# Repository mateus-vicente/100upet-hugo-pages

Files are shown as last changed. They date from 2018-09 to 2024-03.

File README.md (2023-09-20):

---
# 100µPET authors
---

# 100µPET Website

This repository contains the static website pages of the 100µPET project. The deployed website can be found
[here](https://100upet.web.cern.ch).

All commits to the master branch of this repository are automatically deployed to the EOS space of the project and thus
directly reflect on the published website.

## Dependencies

The website is generated from markdown files using the [hugo](https://gohugo.io/) compiler written in Go. In order to
install Hugo on your machine, pick the appropriate package or binary from
[the latest release](https://github.com/gohugoio/hugo/releases).

## Commands
The following commands might help adding content and testing the website locally before committing and deployment:

* __Start a local test server__
    ```sh
    hugo server -D
    ```
    The server will listen to [http://localhost:1313/](http://localhost:1313/).
    The additional command line argument `-D` also enables all documents currently in draft mode.

    Make sure to have the themes fetched as well (`git submodule init && git submodule update --recursive`).

    The repository has to be hosted on the CERN GitLab instance for the CI to work, and the pipeline on the ref has to be
    finished before the script can download the latest artifacts.

* __Add page to the main menu__

    See for example [content/docs/_index.md](./content/docs/_index.md) how to define a page to be in the main menu.

## Deploy Changes

Simply push to the `master` branch of this repository to get things published. It should be noted that only documents with
`draft = false` will be included in the published website.

## Updating Docsy & Prism

* __Docsy__
    To update Docsy (our hugo theme), run
    ```shell
    cd themes/docsy
    git fetch origin --prune
    git checkout origin/HEAD
    ```

* __Prism__
    To update Prism (our code highlighter), visit [this page][@prismdownload] and download `prism.js` and `prism.css` to the
    `static/js` and `static/css` folder respectively. Note that if you change any settings, make sure to update this README
    with the corresponding URL as well.

[@prismdownload]: https://prismjs.com/download.html#themes=prism-tomorrow&languages=clike+bash+c+cpp+cmake+ini+yaml&plugins=autolinker+show-language+toolbar+copy-to-clipboard

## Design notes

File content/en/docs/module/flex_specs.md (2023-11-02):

---
# SPDX-FileCopyrightText: 2022 100µPET
# SPDX-License-Identifier: CC-BY-4.0
title: "Flex Specifications"
weight: 2
---

Each "flex" (or Flexible Printer Circuit - FPC) will have 4 detection ASICs flip-chip bonded (in a 2x2 arrangement) with 300µm between each chip. Each FPC will host small 0201 SMD components in small regions close to the top and bottom peripheries of the 2x2 chip arrangement.

The width of the flex is 300 µm smaller than the width of the 2x2 chip arrangement (i.e. the ASIC hangs 150 µm beyond the flex on 2 edges), to allow an external cooling block to mechanicaly be in contact with the lateral edges of the chips for cooling optimization. 

The data lines and low-voltage power for the ASIC are routed via the a wide flex tail (to be connected to a ZIF connector (<a href="https://www.hirose.com/product/series/FH41">Hirose FH41 series</a>) on the TIM board), while the interface for the sensor biasing HV (200 V, <1 mA) is **yet to be decided**. 

| Main features                     |                                |
|:----------------------------------|:-------------------------------|
| Flex width                        | 60.6 [mm]                      |
| Width of flex's tail              | 20.5 [mm]\*                    |
| Length of flex's tail             | **TBC**                        |
| Number of layers                  | **TBC**                        |
| Number of layers on tail          | <4\*\*                          |
| Gap between ASICs                 | 300 [µm]                       |
| Bonding pads dimensions           | **TBC**\*\*\*                  |

\*See *Connector dimension table*, dimension *F* of connector with 40 pins, at <a href="https://www.hirose.com/en/product/document?clcode=&productname=&series=FH41&documenttype=Catalog&lang=en&documentid=D31607_en">this link</a> </br>
\*\*Single-chip test-flex is not flexible enought with 4 layers. Therefore, the flex's tail should have less. </br>
\*\*\*Pad can be round as the coined gold stud bumps with be smashed round and the diameter (160 microns) should match the uncertainty defined in the requirement for misalignment </br>

Below is the latest layout of the flex.
<object data="../100MuPET_FlexDim.pdf" type="application/pdf" width="100%" height="510px"><p>Here's a link to <a href="CleanCode.pdf">the PDF</a>instead.</p></object>

### Specs **TODO**:
- Shield plate at the back side of the flex with the footprint of the Bi-absorber layer: 
    - Should it be covered with Coverlay? 
        - If not should the Bismuth be glued with a thin adhesive conductive tape? In addition can we leave the Bismuth layer floating (given that the resistivity is 5 order of magnitude higher than copper)?
        - If yes likely to be glued/co-cured with a double-sided  conductive adhesive
    - Shield should be coupled to local ground of the module

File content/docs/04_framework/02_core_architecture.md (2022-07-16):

---
# SPDX-FileCopyrightText: 2022 CERN and the Allpix Squared authors
# SPDX-License-Identifier: CC-BY-4.0
title: "Architecture of the Core"
weight: 2
---

The core is constructed as a light-weight framework which provides various subsystems to the modules. It contains the part of
the software responsible for instantiating and running the modules from the supplied configuration file, and is structured
around five subsystems, of which four are centered around a manager and the fifth contains a set of general utilities. The
systems provided are:

1.  **Configuration**:
    The configuration subsystem provides a configuration object from which data can be retrieved or stored, together with a
    TOML-like \[[@tomlgit]\] parser to read configuration files. It also contains the Allpix Squared configuration manager
    which provides access to the main configuration file and its sections. It is used by the module manager system to find
    the required instantiations and access the global configuration. More information is given in
    [Section 4.3](.././03_configuration).

2.  **Module**:
    The module subsystem contains the base class of all Allpix Squared modules as well as the manager responsible for loading
    and executing the modules (using the configuration system). This component is discussed in more detail in
    [Section 4.4](.././04_modules).

3.  **Geometry**:
    The geometry subsystem supplies helpers for the simulation geometry. The manager instantiates all detectors from the
    detector configuration file. A detector object contains the position and orientation linked to an instantiation of a
    particular detector model, itself containing all parameters describing the geometry of the detector. More details about
    geometry and detector models is provided in [Section 4.5](.././05_geometry_detectors).

4.  **Messenger**:
    The messenger is responsible for sending objects from one module to another. The messenger object is passed to every
    module and can be used to bind to messages to listen for. Messages with objects are also dispatched through the messenger
    as described in [Section 4.6](.././06_messages).

5.  **Utilities**:
    The framework provides a set of utilities for logging, file and directory access, and unit conversion. An explanation on
    how to use of these utilities can be found in [Section 4.8](.././08_logging). A set of C++ exceptions is also provided
    in the utilities, which are inherited and extended by the other components. Proper use of exceptions, together with
    logging information and reporting errors, makes the framework easier to use and debug. A few notes about the use and
    structure of exceptions are provided in [Section 4.9](.././09_error_reporting).

[@tomlgit]: https://github.com/toml-lang/toml

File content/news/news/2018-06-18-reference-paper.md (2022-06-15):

---
# SPDX-FileCopyrightText: 2018 CERN and the Allpix Squared authors
# SPDX-License-Identifier: CC-BY-4.0
title: "Allpix Squared Reference Paper Published"
date: 2018-06-18T11:26:20+02:00
draft: false
---

A paper describing the Allpix Squared framework and providing first validation results using test beam data has just been published in *Nuclear Instrumentations and Methods in Physics Research A*.
The paper is published with open access and can be obtained from here:

https://doi.org/10.1016/j.nima.2018.06.020

Please cite this paper when publishing your work using Allpix Squared as:

> S. Spannagel et al., “Allpix<sup>2</sup>: A modular simulation framework for silicon detectors”, Nucl. Instr.
> Meth. A 901 (2018) 164 – 172, doi:10.1016/j.nima.2018.06.020, arXiv:1806.05813

A preprint version is available on [arxiv.org](https://arxiv.org/abs/1806.05813).

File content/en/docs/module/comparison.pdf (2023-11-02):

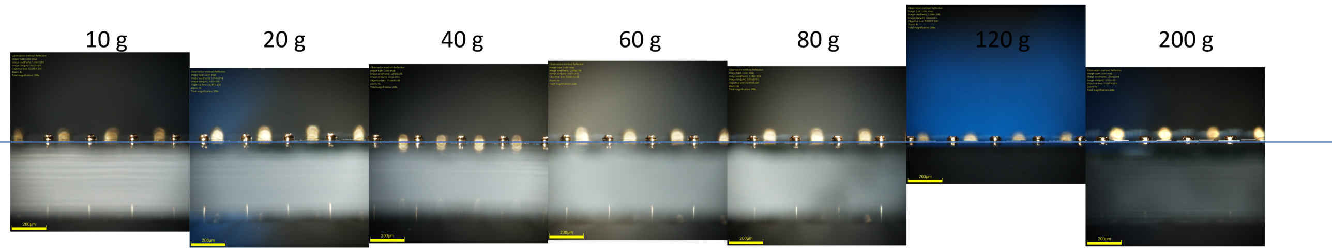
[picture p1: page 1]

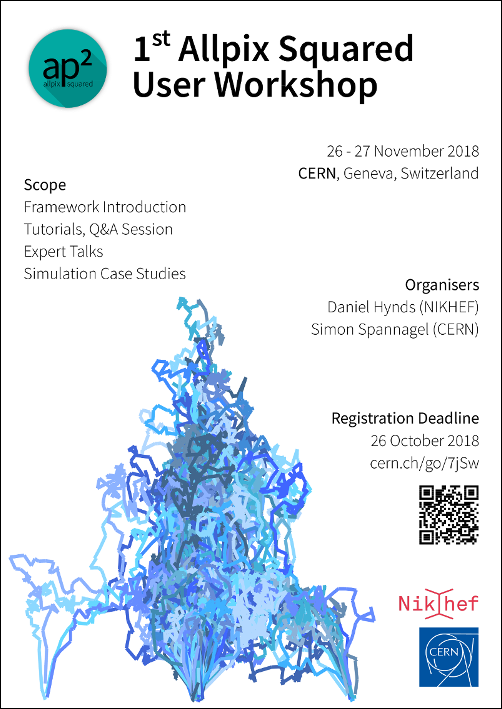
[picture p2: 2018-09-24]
public/img/blog/apsq-workshop-poster.png

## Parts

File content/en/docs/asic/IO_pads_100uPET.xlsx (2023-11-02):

Bottom I/O (periphery side)
 | Counting from left to right
 | Pad pitch on a row: 300 µm
 | Pads staggered on two rows: final pitch 150 µm
 | vertical pitch: | 250 µm
 | Pad size: | 120 x 100
 | Extra distance for HV_sub pads
# | Name | Type | Flex net | # | Name | Type | Flex net | # | Name | Type | Flex net | # | Name | Type | Flex net
1 | HV_SUB | high voltage | HV | 57 | GND_A | ground | GND | 113 | VCC_A | power | VCC_A | 169 | VDD_OSC | power | VDD_DIG
2 | GND_DISC | ground | GND | 58 | VCC_A | power | VCC_A | 114 | GND_DISC | ground | GND | 170 | VSS | ground | GND
3 | VDD_DISC | power | VDD_DIG | 59 | GND_DISC | ground | GND | 115 | VDD_DISC | power | VDD_DIG | 171 | VDD | power | VDD_DIG
4 | THRESHOLD | threshold | THR | 60 | VDD_DISC | power | VDD_DIG | 116 | VDD_OSC | power | VDD_DIG | 172 | GND_A | ground | GND
5 | VDD_OSC | power | VDD_DIG | 61 | VDD_OSC | power | VDD_DIG | 117 | DATA_IN- | LVDS IN | DATA-<i-1> | 173 | VCC_A | power | VCC_A
6 | VSS | ground | GND | 62 | VSS | ground | GND | 118 | DATA_IN+ | LVDS IN | DATA+<i-1> | 174 | GND_DISC | ground | GND
7 | VDD | power | VDD_DIG | 63 | VDD | power | VDD_DIG | 119 | VSS | ground | GND | 175 | VDD_DISC | power | VDD_DIG
8 | GND_A | ground | GND | 64 | GND_A | ground | GND | 120 | DATA_OUT- | LVDS OUT | DATA-<i> | 176 | VDD_OSC | power | VDD_DIG
9 | VCC_A | power | VCC_A | 65 | VCC_A | power | VCC_A | 121 | DATA_OUT+ | LVDS OUT | DATA+<i> | 177 | VSS | ground | GND
10 | GND_DISC | ground | GND | 66 | GND_DISC | ground | GND | 122 | VDD | power | VDD_DIG | 178 | VDD | power | VDD_DIG
11 | VDD_DISC | power | VDD_DIG | 67 | VDD_DISC | power | VDD_DIG | 123 | GND_A | ground | GND | 179 | GND_A | ground | GND
12 | VDD_OSC | power | VDD_DIG | 68 | VDD_OSC | power | VDD_DIG | 124 | VCC_A | power | VCC_A | 180 | VCC_A | power | VCC_A
13 | VSS | ground | GND | 69 | VSS | ground | GND | 125 | GND_DISC | ground | GND | 181 | GND_DISC | ground | GND
14 | VDD | power | VDD_DIG | 70 | VDD | power | VDD_DIG | 126 | VDD_DISC | power | VDD_DIG | 182 | VDD_DISC | power | VDD_DIG
15 | GND_A | ground | GND | 71 | GND_A | ground | GND | 127 | VDD_OSC | power | VDD_DIG | 183 | VDD_OSC | power | VDD_DIG
16 | VCC_A | power | VCC_A | 72 | VCC_A | power | VCC_A | 128 | VSS | ground | GND | 184 | VSS | ground | GND
17 | GND_DISC | ground | GND | 73 | GND_DISC | ground | GND | 129 | RESET_N | CMOS IN | POWER_ON | 185 | VDD | power | VDD_DIG
18 | VDD_DISC | power | VDD_DIG | 74 | VDD_DISC | power | VDD_DIG | 130 | RESET_N_sync- | LVDS IN | RESET_N- | 186 | GND_A | ground | GND
19 | VDD_OSC | power | VDD_DIG | 75 | VDD_OSC | power | VDD_DIG | 131 | RESET_N_sync+ | LVDS IN | RESET_N+ | 187 | VCC_A | power | VCC_A
20 | VSS | ground | GND | 76 | VSS | ground | GND | 132 | VDD | power | VDD_DIG | 188 | GND_DISC | ground | GND
21 | VDD | power | VDD_DIG | 77 | ACK_in | CMOS IN | ACK_C<i+1> | 133 | GND_A | ground | GND | 189 | VDD_DISC | power | VDD_DIG
22 | GND_A | ground | GND | 78 | ACK_out | CMOS OUT | ACK_C<i> | 134 | VCC_A | power | VCC_A | 190 | THRESHOLD | threshold | THR
23 | VCC_A | power | VCC_A | 79 | VDD | power | VDD_DIG | 135 | GND_DISC | ground | GND | 191 | VDD_OSC | power | VDD_DIG
24 | GND_DISC | ground | GND | 80 | GND_A | ground | GND | 136 | VDD_DISC | power | VDD_DIG | 192 | VSS | ground | GND
25 | VDD_DISC | power | VDD_DIG | 81 | VCC_A | power | VCC_A | 137 | VDD_OSC | power | VDD_DIG | 193 | VDD | power | VDD_DIG
26 | VDD_OSC | power | VDD_DIG | 82 | GND_DISC | ground | GND | 138 | VSS | ground | GND | 194 | GND_A | ground | GND
27 | VSS | ground | GND | 83 | VDD_DISC | power | VDD_DIG | 139 | SPI_MOSI | CMOS IN | SPI_MOSI | 195 | VCC_A | power | VCC_A
28 | VDD | power | VDD_DIG | 84 | VDD_OSC | power | VDD_DIG | 140 | SPI_CLK | CMOS IN | SPI_CLK | 196 | HV_SUB | high voltage | HV
29 | GND_A | ground | GND | 85 | VSS | ground | GND | 141 | SPI_CS | CMOS IN | SPI_CS
30 | VCC_A | power | VCC_A | 86 | Req_in | CMOS IN | Req<i-1> | 142 | SPI_MISO | CMOS OUT | N/A
31 | GND_DISC | ground | GND | 87 | Req_out | CMOS OUT | Req<i> | 143 | VDD | power | VDD_DIG
32 | VDD_DISC | power | VDD_DIG | 88 | VDD | power | VDD_DIG | 144 | GND_A | ground | GND
33 | VDD_OSC | power | VDD_DIG | 89 | GND_A | ground | GND | 145 | VCC_A | power | VCC_A
34 | VSS | ground | GND | 90 | VCC_A | power | VCC_A | 146 | GND_DISC | ground | GND
35 | VDD | power | VDD_DIG | 91 | GND_DISC | ground | GND | 147 | VDD_DISC | power | VDD_DIG
36 | GND_A | ground | GND | 92 | VDD_DISC | power | VDD_DIG | 148 | VDD_OSC | power | VDD_DIG
37 | VCC_A | power | VCC_A | 93 | VDD_OSC | power | VDD_DIG | 149 | VSS | ground | GND
38 | GND_DISC | ground | GND | 94 | CHIP_ID_0 | POWER/GND | GND/VDD_DIG | 150 | VDD | power | VDD_DIG
39 | VDD_DISC | power | VDD_DIG | 95 | CHIP_ID_1 | POWER/GND | GND/VDD_DIG | 151 | GND_A | ground | GND
40 | VDD_OSC | power | VDD_DIG | 96 | CHIP_ID_2 | POWER/GND | GND/VDD_DIG | 152 | VCC_A | power | VCC_A
41 | VSS | ground | GND | 97 | VSS | ground | GND | 153 | GND_DISC | ground | GND
42 | VDD | power | VDD_DIG | 98 | TRIG_SLOW- | LVDS OUT | N/A | 154 | VDD_DISC | power | VDD_DIG
43 | GND_A | ground | GND | 99 | TRIG_SLOW+ | LVDS OUT | N/A | 155 | VDD_OSC | power | VDD_DIG
44 | VCC_A | power | VCC_A | 100 | TRIG_FAST- | LVDS OUT | N/A | 156 | VSS | ground | GND
45 | GND_DISC | ground | GND | 101 | TRIG_FAST+ | LVDS OUT | N/A | 157 | VDD | power | VDD_DIG
46 | VDD_DISC | power | VDD_DIG | 102 | VDD | power | VDD_DIG | 158 | GND_A | ground | GND
47 | VDD_OSC | power | VDD_DIG | 103 | GND_A | ground | GND | 159 | VCC_A | power | VCC_A
48 | VSS | ground | GND | 104 | VCC_A | power | VCC_A | 160 | GND_DISC | ground | GND
49 | VDD | power | VDD_DIG | 105 | GND_DISC | ground | GND | 161 | VDD_DISC | power | VDD_DIG
50 | GND_A | ground | GND | 106 | VDD_DISC | power | VDD_DIG | 162 | VDD_OSC | power | VDD_DIG
51 | GR0 | GuardRing | VCC_A | 107 | VDD_OSC | power | VDD_DIG | 163 | VSS | ground | GND
52 | GND_DISC | ground | GND | 108 | VSS | ground | GND | 164 | VDD | power | VDD_DIG
53 | VDD_DISC | power | VDD_DIG | 109 | RO_CLK- | LVDS IN | RO_CLK- | 165 | GND_A | ground | GND
54 | VDD_OSC | power | VDD_DIG | 110 | RO_CLK+ | LVDS IN | RO_CLK+ | 166 | VCC_A | power | VCC_A
55 | VSS | ground | GND | 111 | VDD | power | VDD_DIG | 167 | GND_DISC | ground | GND
56 | VDD | power | VDD_DIG | 112 | GND_A | ground | GND | 168 | VDD_DISC | power | VDD_DIG
Top I/O (power only)
 | Counting from left to right
 | Pad pitch on a row: 300 µm
 | Pad size: | 120 x 100
 | Extra distance for HV_sub pads
# | Name | Type | Flex net | # | Name | Type | Flex net | # | Name | Type | Flex net | # | Name | Type | Flex net
197 | HV_SUB | high voltage | HV | 225 | VDD | power | VDD_DIG | 253 | VDD_DISC | power | VDD_DIG | 281 | VCC_A | power | VCC_A
198 | GND_DISC | ground | GND | 226 | GND_A | ground | GND | 254 | VSS | ground | GND | 282 | GND_DISC | ground | GND
199 | VDD_DISC | power | VDD_DIG | 227 | VCC_A | power | VCC_A | 255 | VDD | power | VDD_DIG | 283 | VDD_DISC | power | VDD_DIG
200 | VSS | ground | GND | 228 | GND_DISC | ground | GND | 256 | GND_A | ground | GND | 284 | VSS | ground | GND
201 | VDD | power | VDD_DIG | 229 | VDD_DISC | power | VDD_DIG | 257 | VCC_A | power | VCC_A | 285 | VDD | power | VDD_DIG
202 | GND_A | ground | GND | 230 | VSS | ground | GND | 258 | GND_DISC | ground | GND | 286 | GND_A | ground | GND
203 | VCC_A | power | VCC_A | 231 | VDD | power | VDD_DIG | 259 | VDD_DISC | power | VDD_DIG | 287 | VCC_A | power | VCC_A
204 | GND_DISC | ground | GND | 232 | GND_A | ground | GND | 260 | VSS | ground | GND | 288 | GND_DISC | ground | GND
205 | VDD_DISC | power | VDD_DIG | 233 | VCC_A | power | VCC_A | 261 | VDD | power | VDD_DIG | 289 | VDD_DISC | power | VDD_DIG
206 | VSS | ground | GND | 234 | GND_DISC | ground | GND | 262 | GND_A | ground | GND | 290 | VSS | ground | GND
207 | VDD | power | VDD_DIG | 235 | VDD_DISC | power | VDD_DIG | 263 | VCC_A | power | VCC_A | 291 | VDD | power | VDD_DIG
208 | GND_A | ground | GND | 236 | VSS | ground | GND | 264 | GND_DISC | ground | GND | 292 | GND_A | ground | GND
209 | VCC_A | power | VCC_A | 237 | VDD | power | VDD_DIG | 265 | VDD_DISC | power | VDD_DIG | 293 | VCC_A | power | VCC_A
210 | GND_DISC | ground | GND | 238 | GND_A | ground | GND | 266 | VSS | ground | GND | 294 | THRESHOLD | threshold | THR
211 | VDD_DISC | power | VDD_DIG | 239 | VCC_A | power | VCC_A | 267 | VDD | power | VDD_DIG | 295 | HV_SUB | high voltage | HV
212 | VSS | ground | GND | 240 | GND_DISC | ground | GND | 268 | GND_A | ground | GND
213 | VDD | power | VDD_DIG | 241 | VDD_DISC | power | VDD_DIG | 269 | VCC_A | power | VCC_A
214 | GND_A | ground | GND | 242 | VSS | ground | GND | 270 | GND_DISC | ground | GND
215 | VCC_A | power | VCC_A | 243 | VDD | power | VDD_DIG | 271 | VDD_DISC | power | VDD_DIG
216 | GND_DISC | ground | GND | 244 | GND_A | ground | GND | 272 | VSS | ground | GND
217 | VDD_DISC | power | VDD_DIG | 245 | VCC_A | power | VCC_A | 273 | VDD | power | VDD_DIG
218 | VSS | ground | GND | 246 | GND_DISC | ground | GND | 274 | GND_A | ground | GND
219 | VDD | power | VDD_DIG | 247 | VDD_DISC | power | VDD_DIG | 275 | VCC_A | power | VCC_A
220 | GND_A | ground | GND | 248 | VSS | ground | GND | 276 | GND_DISC | ground | GND
221 | VCC_A | power | VCC_A | 249 | VDD | power | VDD_DIG | 277 | VDD_DISC | power | VDD_DIG
222 | GND_DISC | ground | GND | 250 | GND_A | ground | GND | 278 | VSS | ground | GND
223 | VDD_DISC | power | VDD_DIG | 251 | VCC_A | power | VCC_A | 279 | VDD | power | VDD_DIG
224 | VSS | ground | GND | 252 | GND_DISC | ground | GND | 280 | GND_A | ground | GND

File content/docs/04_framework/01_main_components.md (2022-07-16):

---
# SPDX-FileCopyrightText: 2022 CERN and the Allpix Squared authors
# SPDX-License-Identifier: CC-BY-4.0
title: "Main Components"
weight: 1
---

The framework consists of the following four main components that together form Allpix Squared:

1.  **Core**:
    The core contains the internal logic to initialize the modules, provide the geometry, facilitate module communication and
    run the event sequence. The core keeps its dependencies to a minimum (it only relies on ROOT) and remains independent
    from the other components as far as possible. It is the main component discussed in this section.

2.  **Modules**:
    A module is a set of methods which is executed as part of the simulation chain. Modules are built as separate libraries
    and loaded dynamically on demand by the core. The available modules and their parameters are discussed in detail in
    [Chapter 7](../../07_modules).

3.  **Objects**:
    Objects form the data passed between modules using the message framework provided by the core. Modules can listen and
    bind to messages with objects they wish to receive. Messages are identified by the object type they are carrying, but can
    also be renamed to allow the direction of data to specific modules, facilitating more sophisticated simulation setups.
    Messages are intended to be read-only and a copy of the data should be made if a module wishes to change the data. All
    objects are compiled into a separate library which is automatically linked to every module. More information about the
    messaging system and the supported objects can be found in [Section 4.6](.././06_messages).

4.  **Physics**:
    In many cases, several modules depend on the same underlying physics models. These models are separated from the modules
    themselves. The implemented physics models are described in [Chapter 5](../../05_models).

5.  **Tools**:
    Allpix Squared provides a set of header-only 'tools' and a shared library that allow access to common logic shared by
    various modules. Examples are the Runge-Kutta solver \[[@fehlberg]\] implemented using the Eigen3 library and the set of
    template specializations for ROOT and Geant4 configurations. More information about the tools can be found in
    [Chapter 13](../../13_additional). This set of tools is different from the set of core utilities the framework
    itself provides, which is part of the core and explained in [Section 4.8](.././08_logging).

Finally, Allpix Squared provides an executable which instantiates the core of the framework, receives and distributes the
configuration object and runs the simulation chain.

The chapter is structured as follows. [Section 4.2](.././02_core_architecture) provides an overview of the architectural
design of the core and describes its interaction with the rest of the Allpix Squared framework. The different subcomponents
such as configuration, modules and messages are discussed in thereafter. The chapter closes with a description of the
available framework tools in [Section 4.8](.././08_logging). Some C++ code will be provided in the text, but readers not
interested may skip the technical details.

[@fehlberg]: https://ntrs.nasa.gov/search.jsp?R=19690021375

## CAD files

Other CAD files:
content/en/app/models_and_data/Mouse_phantom_AA_80x19x34_1000um.3dm
content/en/app/models_and_data/Mouse_phantom_A_80x19x34_1000um.3dm
content/en/app/models_and_data/Mouse_phantom_BB_160x38x68_500um.3dm
content/en/app/models_and_data/Mouse_phantom_B_160x38x68_500um.3dm
content/en/app/models_and_data/Plaque_000Bi_100x100x100_100um.3dm
content/en/app/models_and_data/Plaque_050Bi_100x100x100_100um.3dm
content/en/app/models_and_data/Plaque_template_200x60x60_50um.3dm
content/en/app/models_and_data/plaque_and_full_noise_resamp_68x34x34_1000um.3dm

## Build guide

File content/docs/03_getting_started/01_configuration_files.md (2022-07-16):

---
# SPDX-FileCopyrightText: 2022 CERN and the Allpix Squared authors
# SPDX-License-Identifier: CC-BY-4.0
title: "Configuration Files"
weight: 1
---

The framework is configured with simple human-readable configuration files. The configuration format is described in detail
in [Section 4.3](../../04_framework/03_configuration#file-format). It consists of several section headers within `[` and `]`
brackets, and a section without header at the start. Each of these sections contains a set of key/value pairs separated by
the `=` character. Comments are indicated using the hash symbol (`#`).

The framework has the following three required layers of configuration files:

- The **main** configuration:
  The most important configuration file and the file that is passed directly to the binary. Contains both the global
  framework configuration and the list of modules to instantiate together with their configuration. An example can be found
  in the repository at `examples/example.conf`. More details and a more thorough example are found in
  [Section 3.2](.././02_main_configuration), several advanced simulation chain configurations are presented in
  [Chapter 8](../../08_examples).

- The **geometry** configuration:
  It is passed to the framework to determine the detector setup and passive materials. Describes the detector setup,
  containing the position, orientation and model type of all detectors. Optionally, passive materials can be added to this
  configuration. Examples are available in the repository at `examples/ example_detector.conf` or
  `examples/example_detector_passive.conf`. Introduced in [Section 3.3](.././03_detector_configuration).

- The detector **model** configuration:
  Contains the parameters describing a particular type of detector. Several models are already provided by the framework,
  but new types of detectors can easily be added. See `models/test.conf` in the repository for an example. Please refer to
  [Section 9.5](../../09_development/05_new_detector_model) for more details about adding new models.

## Parsing Types and Units

The Allpix Squared framework supports the use of a variety of types for all configuration values. The module specifies how
the value type should be interpreted. An error will be raised if either the key is not specified in the configuration file,
the conversion to the desired type is not possible, or if the given value is outside the domain of possible options. Please
refer to the [Chapter 7](../../07_modules) for the list of module parameters and their types. Parsing the value
roughly follows common-sense (more details can be found in
[Section 4.3](../../04_framework/03_configuration#accessing-parameters)). A few special rules do apply:

- If the value is a **string**, it may be enclosed by a single pair of double quotation marks (`"`), which are stripped
  before passing the value to the modules. If the string is not enclosed by quotation marks, all whitespace before and
  after the value is erased. If the value is an array of strings, the value is split at every whitespace or comma (`,`)
  that is not enclosed in quotation marks.

- If the value is a **boolean**, either numerical (`0`, `1`) or textual (`false`, `true`) representations are accepted.

- If the value is a **relative path**, that path will be made absolute by adding the absolute path of the directory that
  contains the configuration file where the key is defined.

- If the value is an **arithmetic** type, it may have a suffix indicating the unit. The list of base units is given in the
  table below.

| Quantity                | Default unit                   | Auxiliary units                                                                                                      |
|:------------------------|:-------------------------------|:---------------------------------------------------------------------------------------------------------------------|
| Unity                   | 1                              | -                                                                                                                    |
| Length                  | mm (millimeter)                | nm (nanometer), <br> um (micrometer), <br> cm (centimeter), <br> dm (decimeter), <br> m (meter), <br> km (kilometer) |
| Time                    | ns (nanosecond)                | ps (picosecond), <br> us (microsecond), <br> ms (millisecond), <br> s (second)                                       |
| Energy                  | MeV (megaelectronvolt)         | eV (electronvolt), <br> keV (kiloelectronvolt), <br> GeV (gigaelectronvolt)                                          |
| Temperature             | K (kelvin)                     | -                                                                                                                    |
| Charge                  | e (elementary charge)          | ke (kiloelectrons), <br> fC (femtocoulomb), <br> C (coulomb)                                                         |
| Voltage                 | MV (megavolt)                  | V (volt), <br> kV (kilovolt)                                                                                         |
| Magnetic field strength | T (tesla)                      | mT (millitesla)                                                                                                      |
| Angle                   | rad (radian)                   | deg (degree), <br> mrad (milliradian)                                                                                |
| Radiation fluence       | Neq (1-MeV neutron-equivalent) | -                                                                                                                    |

{{% alert title="Warning" color="warning" %}}
If no units are specified, values will always be interpreted in the base units of the framework. In some cases this can lead
to unexpected results. E.g. specifying a bias voltage as `bias_voltage = 50` results in an applied voltage of 50 MV.
Therefore it is strongly recommended to always specify units in the configuration files.
{{% /alert %}}

The internal base units of the framework are not chosen for user convenience but for maximum precision of the calculations
and in order to avoid the necessity of conversions in the code.

Combinations of base units can be specified by using the multiplication sign `*` and the division sign `/` that are parsed in
linear order (thus $`\frac{V m}{s^2}`$ should be specified as `V*m/s/s`). The framework assumes the default units if the unit
is not explicitly specified. It is recommended to always specify the unit explicitly for all parameters that are not
dimensionless as well as for angles.

Examples of specifying key/values pairs of various types are given below:

```ini
# All whitespace at the front and back is removed
first_string =   string_without_quotation
# All whitespace within the quotation marks is preserved
second_string = "  string with quotation marks  "
# Keys are split on whitespace and commas
string_array = "first element" "second element","third element"
# Elements of matrices with more than one dimension are separated
# using square brackets
string_matrix_3x3 = [["1","0","0"], ["0","cos","-sin"], ["0","sin",cos]]
# If the matrix is of dimension 1xN, the outer brackets have to be
# added explicitly
integer_matrix_1x3 = [[10, 11, 12]]
# Integer and floats can be specified in standard formats
int_value = 42
float_value = 123.456e9
# Units can be passed to arithmetic types
energy_value = 1.23MeV
time_value = 42ns
# Units are combined in linear order without grouping or implicit brackets
acceleration_value = 1.0m/s/s
# Thus the quantity below is the same as 1.0deg*kV*K/m/s
random_quantity = 1.0deg*kV/m/s*K
# Relative paths are expanded to absolute paths, e.g. the following value
# will become "/home/user/test" if the configuration file is located
# at "/home/user"
output_path = "test"
# Booleans can be represented in numerical or textual style
my_switch = true
my_other_switch = 0
```

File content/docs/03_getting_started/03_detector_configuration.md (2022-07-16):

---
# SPDX-FileCopyrightText: 2022 CERN and the Allpix Squared authors
# SPDX-License-Identifier: CC-BY-4.0
title: "Detector Configuration"
weight: 3
---

The detector configuration consists of a set of sections describing the detectors in the setup. Each section starts with a
header describing the name used to identify the detector; all names are required to be unique. Every detector has to contain
all of the following parameters:

- A string referring to the `type` of the detector model. The model should exist in the search path as described in
  [Section 4.5](../../04_framework/05_geometry_detectors#detector-models).

- The 3-dimensional `position` in the world frame in the order x, y, z. See
  [Section 4.5](../../04_framework/05_geometry_detectors) for details.

- The `orientation` specified as X-Y-Z extrinsic Euler angles. This means the detector is rotated first around the world's
  X-axis, then around the world's Y-axis and then around the world's Z-axis. Alternatively the orientation can be set as
  Z-Y-X or Z-X-Z extrinsic Euler angles, refer to section [Section 4.5](../../04_framework/05_geometry_detectors) for
  details.

In addition to these required parameters, the following parameters allow to randomly misalign the respective detector from
its initial position. The values are interpreted as width of a normal distribution centered around zero. In order to
reproduce misalignments, a fixed random seed for the framework core can be used as explained in
[Section 3.4](.././04_framework_parameters). Misalignment can be introduced both for shifts along the three global axes and
the three rotations angles with the following parameters:

- The parameter `alignment_precision_position` allows the specification of the alignment precision along the three global
  axes. Each value represents the Gaussian width with which the detector will be randomly misaligned along the
  corresponding axis.

- The parameter `alignment_precision_orientation` allows to specify the alignment precision in the three rotation angles
  defined by the `orientation` parameter. The misalignments are added to the individual angles before combining them into
  the final rotation as defined by the `orientation_mode` parameter.

The optional parameter `role` accepts the values `active` for detectors and `passive` for passive elements in the setup. If
no value is given, `active` is taken as the default value.

Furthermore it is possible to specify certain parameters of the detector, which is explained in more detail in
[Section 4.5](../../04_framework/05_geometry_detectors#detector-models). This allows to quickly adapt e.g. the sensor
thickness of a certain detector without altering the actual detector model file.

An example configuration file describing a setup with one CLICpix2 detector and two Timepix \[[@timepix]\] models is the
following:

```ini
# Placement of first detector, named "telescope1"
[telescope1]
# Type to the detector is the "timepix" model
type = "timepix"
# Position the detector at the origin of the world frame
position = 0 0 0mm
# Default orientation: perpendicular to the incoming beam
orientation = 0 0 0

# Placement of the second detector, the "DUT (device under test)
[dut]
# Detector model is "clicpix2"
type = "clicpix2"
# Position is downstream of "telescope1":
position = 100um 100um 25mm
# Rotated by 20 degrees around the world x-axis
orientation = 20deg 0 0

# Third detector is downstream "telescope2"
[telescope2]
# Detector type again is "timepix"
type = "timepix"
# Placement 50 mm downstream of the first detector
position = 0 0 50mm
# Default orientation
orientation = 0 0 0
```

This configuration is used in the rest of this chapter for explaining concepts. A visualization of the setup is given below.

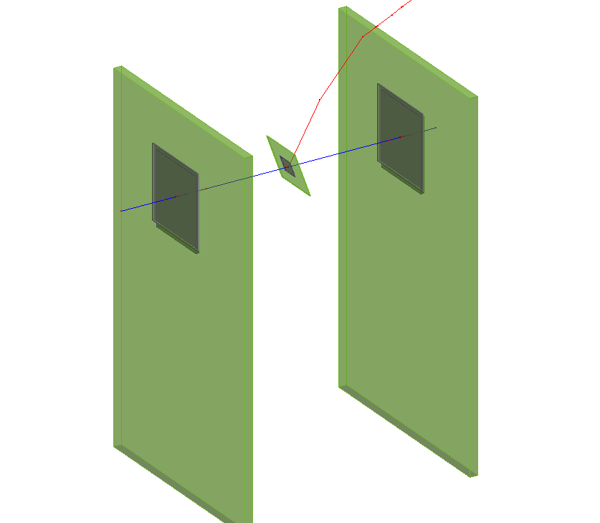
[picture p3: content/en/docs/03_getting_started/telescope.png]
\
*Visualization of a Pion passing through the telescope setup defined in the detector configuration file. A secondary particle
is produced in the material of the detector in the center.*

## Passive material configuration

Descriptions of passive materials can be added to the detector setup via a set of sections, with a syntax similar to the
detector configuration. Passive geometry entries are identified by the `role` parameter set to `passive`. Each section starts
with a header describing the name used to identify the passive material; all names are required to be unique.

Every passive material has to contain all of the following parameters:

- The `position` and `orientation` of the material as described for the detector, see
  [Section 3.3](.././03_detector_configuration).

- A string referring to the `type` of the passive material. The model should be interpreted by the module constructing the
  passive material, such as for example the
  [`GeometryBuilderGeant4` module](../../07_modules/geometrybuildergeant4#passive-volumes).

- A string referring to the `material` of the passive material. The materials for the `GeometryBuilderGeant4` module are
  defined in the [module documentation](../../07_modules/geometrybuildergeant4#materials).

- A set of size parameters specific for the model that is chosen. All size parameters that describe the total length of
  something are placed such that half of this total length extends from each side of the given `position`. If a parameter
  describes the radius, this means the radius will extend from the `position` on both sides, making its total size two
  times the radius in the given direction. The size parameters for the specific models in the `GeometryBuilderGeant4`
  module are described in the [module documentation](../../07_modules/geometrybuildergeant4#passive-volumes).

In addition, an optional string referring to the `mother_volume`, which defines another passive material the volume will be
placed in, can be specified.

{{% alert title="Note" color="info" %}}
If a mother volume is chosen, the position defined in the configuration file will be relative to the center of the mother
volume. An error will be given if the specified mother volume is too small for the specified size or position of this volume.
Per default, the mother volume is the world frame.
{{% /alert %}}

{{% alert title="Note" color="info" %}}
If the `mother_volume` is a hollow material, only the non-hollow part of the material is considered part of the material.
Placing a passive volume in the hollow part requires a different `mother_volume`.
{{% /alert %}}

Similar to the detector configuration, the parameters `orientation_mode` (see
[Section 4.5](../../04_framework/05_geometry_detectors)), `alignment_precision_position` and
`alignment_precision_orientation` (see [Section 3.3](.././03_detector_configuration)) can be used optionally to define the
rotation order and a possible misalignment of passive materials.

An example configuration file describing a set of passive materials with different configuration options is the following:

```ini
# Placement of a box made of lead
[box1]
type = "box"
size = 100mm 100mm 100mm
position = 200mm 200mm 0mm
orientation = 0 0deg 0deg
material = "lead"
role = "passive"

# Placement of a box made of lead
[box2]
type = "box"
size = 100mm 100mm 100mm
position = 0mm 200mm 0mm
orientation = 0 0deg 0deg
material = "lead"
role = "passive"

# Placement of a box made of lead, with a hollow opening
[box3]
type = "box"
size = 100mm 100mm 100mm
inner_size = 80mm 80mm 100mm
position = -200mm 200mm 0mm
orientation = 0 0deg 0deg
material = "lead"
role = "passive"

# Placement of a box made of aluminum, inside box1
[box4]
type = "box"
size = 50mm 50mm 50mm
position = 0mm 0mm -0mm
orientation = 0 0deg 0deg
material = "aluminum"
mother_volume = box1
role = "passive"

# Placement of a box made of the world material, inside box2
[box5]
type = "box"
size = 50mm 50mm 50mm
position = 0mm 0mm -0mm
orientation = 0 0deg 0deg
material = "world_material"
mother_volume = box2
role = "passive"

# Placement of a cylinder made of lead, with a hollow opening
[cylinder1]
type = "cylinder"
outer_radius = 50mm
inner_radius = 40mm
length = 100mm
position = 200mm 0mm 0mm
orientation = 0 0deg 0deg
material = "lead"
role = "passive"

# Placement of a cylinder made of lead
[cylinder2]
type = "cylinder"
outer_radius = 50mm
length = 100mm
position = 0mm 0mm 0mm
orientation = 0 0deg 0deg
material = "lead"
role = "passive"

# Placement of a cylinder made of lead, with a hollow opening, starting the building at an angle of 60deg and continue for 270deg
[cylinder3]
type = "cylinder"
outer_radius = 50mm
inner_radius = 20mm
length = 100mm
starting_angle = 60deg
arc_length = 270deg
position = -200mm 0mm 0mm
orientation = 0 0deg 0deg
material = "lead"
role = "passive"

# Placement of a cylinder made of the world material, inside cylinder2
[cylinder4]
type = "cylinder"
outer_radius = 25mm
length = 50mm
position = 0mm 0mm 0mm
orientation = 0 0deg 0deg
material = "world_material"
mother_volume = cylinder2
role = "passive"

# Placement of a sphere made of lead
[sphere1]
type = "sphere"
outer_radius = 50mm
position = 200mm -200mm 0mm
orientation = 0 0deg 0deg
material = "lead"
role = "passive"

# Placement of a sphere made of lead,  with a hollow opening, starting the building at a phi angle of 90deg and continue for 180deg.
[sphere2]
type = "sphere"
outer_radius = 50mm
inner_radius = 30mm
starting_angle_phi = 90deg
arc_length_phi = 180deg
position = 0mm -200mm 0mm
orientation = 0 0deg 0deg
material = "lead"
role = "passive"

# Placement of a sphere made of lead, starting the building at a theta angle of 0deg and continue for 45deg.
[sphere3]
type = "sphere"
outer_radius = 50mm
arc_length_theta = 45deg
position = -200mm -200mm 0mm
orientation = 0 -90deg 0deg
material = "lead"
role = "passive"
```

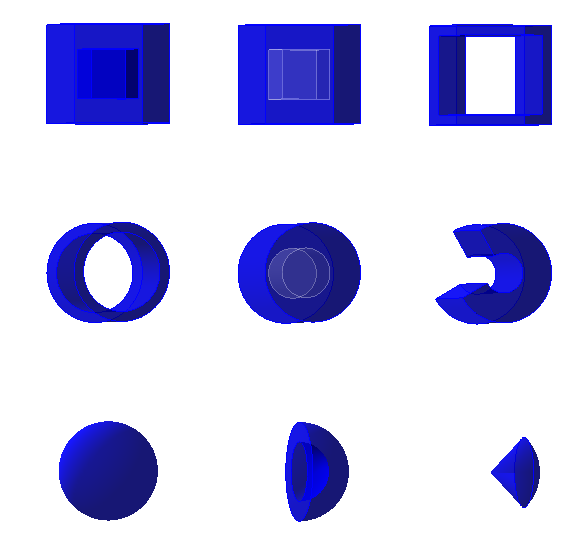
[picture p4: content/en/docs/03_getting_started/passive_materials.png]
\
*Visualization of the setup described in the geometry file.*

[@timepix]: https://doi.org/10.1016/j.nima.2007.08.079

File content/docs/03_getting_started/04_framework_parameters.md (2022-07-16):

---
# SPDX-FileCopyrightText: 2022 CERN and the Allpix Squared authors
# SPDX-License-Identifier: CC-BY-4.0
title: "Framework Parameters"
weight: 4
---

The Allpix Squared framework provides a set of global parameters which control and alter its behavior:

- `detectors_file`:
  Location of the file describing the detector configuration (introduced in [Section 3.3](.././03_detector_configuration)).
  The only *required* global parameter: the framework will fail to start if it is not specified.

- `number_of_events`:
  Determines the total number of events the framework should simulate. Defaults to one (simulating a single event).

- `skip_events`:
  A number of events (and therefore event seeds) to be skipped at start of the run. After skipping, the full
  `number_of_events` will be processed starting from the new event seed. Defaults to zero, i.e. starting with the first
  event seed.

- `root_file`:
  Location relative to the `output_directory` where the ROOT output data of all modules will be written to. The file
  extension `.root` will be appended if not present. Default value is `modules.root`. Directories within the ROOT file will
  be created automatically for all module instantiations.

- `log_level`:
  Specifies the lowest log level which should be reported. Possible values are `FATAL`, `STATUS`, `ERROR`, `WARNING`,
  `INFO`, `DEBUG`, `TRACE` and `PRNG` where all options are case-insensitive. Defaults to the `WARNING` level. More details
  and information about the log levels, including how to change them for a particular module, can be found in
  [Section 3.8](.././08_logging_and_verbosity). Can be overwritten by the `-v` parameter on the command line (see
  [Section 3.5](.././05_allpix_executable)).

- `log_format`:
  Determines the log message format to display. Possible options are `SHORT`, `DEFAULT` and `LONG`, where all options are
  case-insensitive. More information can be found in [Section 3.8](.././08_logging_and_verbosity).

- `log_file`:
  File where the log output should be written to in addition to printing to the standard output (usually the terminal).
  Only writes to standard output if this option is not provided. Another (additional) location to write to can be specified
  on the command line using the `-l` parameter (see [Section 3.5](.././05_allpix_executable)).

- `output_directory`:
  Directory to write all output files into. Subdirectories are created automatically for all module instantiations. This
  directory will also contain the `root_file` specified via the parameter described above. Defaults to the current working
  directory with the subdirectory `output/` attached.

- `purge_output_directory`:
  Decides whether the content of an already existing output directory is deleted before a new run starts. Defaults to
  `false`, i.e. files are kept but will be overwritten by new files created by the framework.

- `deny_overwrite`:
  Forces the framework to abort the run and throw an exception when attempting to overwrite an existing file. Defaults to
  `false`, i.e. files are overwritten when requested. This setting is inherited by all modules, but can be overwritten in
  the configuration section of each of the modules.

- `random_seed`:
  Seed for the global random seed generator used to initialize seeds for module instantiations. The 64-bit Mersenne Twister
  `mt19937_64` from the C++ Standard Library is used to generate seeds. A random seed from multiple entropy sources will be
  generated if the parameter is not specified. Can be used to reproduce an earlier simulation run.

- `random_seed_core`:
  Optional seed used for pseudo-random number generators in the core components of the framework. If not set explicitly,
  the value `random_seed + 1` is used.

- `library_directories`:
  Additional directories to search for module libraries, before searching the default paths. See
  [Section 4.4](../../04_framework/04_modules#module-instantiation) for more information.

- `model_paths`:
  Additional files or directories from which detector models should be read besides the standard search locations.

- `performance_plots`:
  Enable the creation of performance plots showing the processing time required per event both for individual modules and
  the full module stack. Defaults to `false`.

- `multithreading`:
  Enable multithreading for the framework. Defaults to `true`. More information about multithreading can be found in
  [Section 4.3](../../04_framework/04_modules#multithreading-parallel-execution-of-events).

- `workers`:
  Specify the number of workers to use in total, should be strictly larger than zero. Only used if `multithreading` is set
  to `true`. Defaults to the number of native threads available on the system minus one, if this can be determined,
  otherwise one thread is used.

- `buffer_per_worker`:
  Specify the buffer depth available per worker for buffered modules to cache partially processed events until execution in
  the correct order can be guaranteed (see [Section 4.10](../../04_framework/10_multithreading)). Defaults to `256`.

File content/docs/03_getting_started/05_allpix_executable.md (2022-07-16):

---
# SPDX-FileCopyrightText: 2022 CERN and the Allpix Squared authors
# SPDX-License-Identifier: CC-BY-4.0
title: "The allpix Executable"
weight: 5
---

The `allpix` executable functions as the interface between the user and the framework. It is primarily used to provide the
main configuration file, but also allows to add and overwrite options from the main configuration file. This is both useful
for quick testing as well as for batch processing of simulations.

The executable handles the following arguments:

- `-c <file>`:
  Specifies the configuration file to be used for the simulation, relative to the current directory. This is the only
  *required* argument, the simulation will fail to start if this argument is not given.

- `-l <file>`:
  Specify an additional location to forward log output to, besides standard output and the location specified in the
  framework parameters explained in [Section 3.4](.././04_framework_parameters).

- `-v <level>`:
  Sets the global log verbosity level, overwriting the value specified in the configuration file described in
  [Section 3.4](.././04_framework_parameters). Possible values are `FATAL`, `STATUS`, `ERROR`, `WARNING`, `INFO` and
  `DEBUG`, `TRACE` and `PRNG` where all options are case-insensitive. The module specific logging level introduced in
  [Section 3.8](.././08_logging_and_verbosity) is not overwritten.

- `-j <workers>`:
  Enables multithreaded event processing with the given number of worker threads. This is equivalent to passing the
  framework parameters `-o multithreading=true -o workers=<workers>` to the executable.

- `--version`:
  Prints the version and build time of the executable and terminates the program.

- `-o <option>`:
  Passes extra framework or module options which are added and overwritten in the main configuration file. This argument
  may be specified multiple times, to add multiple options. Options are specified as key/value pairs in the same syntax as
  used in the configuration files (refer to [Section 4.2](../../04_framework/03_configuration#file-format) for more
  details), but the key is extended to include a reference to a configuration section or instantiation in shorthand
  notation. There are three types of keys that can be specified:

  - Keys to set **framework parameters**:
    These have to be provided in exactly the same way as they would be in the main configuration file (a section does not
    need to be specified). An example to overwrite the standard output directory would be
    `allpix -c <file> -o output_directory="run123456"`.

  - Keys for **module configurations**:
    These are specified by adding a dot (`.`) between the module and the actual key as it would be given in the
    configuration file (thus `module.key`). An example to overwrite the deposited particle to a positron would be
    `allpix -c <file> -o DepositionGeant4.particle_type="e+"`.

  - Keys to specify values for a particular **module instantiation**:
    The identifier of the instantiation and the name of the actual key are split by a dot (`.`), in the same way as for
    keys for module configurations (thus `identifier.key`). The unique identifier for a module can contains one or more
    colons (`:`) to distinguish between various instantiations of the same module. The exact name of an identifier
    depends on the name of the detector and the optional input and output name. Those identifiers can be extracted from
    the logging section headers. An example to change the temperature of propagation for a particular instantiation for a
    detector named `dut` could be `allpix -c <file> -o GenericPropagation:dut.temperature=273K`.

  Note that only the single argument directly following the `-o` is interpreted as the option. If there is whitespace in
  the key/value pair this should be properly enclosed in quotation marks to ensure the argument is parsed correctly.

- `-g <option>`:
  Passes extra detector options which are added and overwritten in the detector configuration file. This argument can be
  specified multiple times, to add multiple options. The options are parsed in the same way as described above for module
  options, but only one type of key can be specified to overwrite an option for a single detector. These are specified by
  adding a dot (`.`) between the detector and the actual key as it would be given in the detector configuration file (thus
  `detector.key`). This method also works for customizing detector models as described in
  [Section 4.5](../../04_framework/05_geometry_detectors#detector-models). An example to overwrite the sensor thickness for
  a particular detector named `detector1` to `50um` would be `allpix -c <file> -g detector1.sensor_thickness=50um`.

No interaction with the framework is possible during the simulation. Signals can however be send using keyboard shortcuts to
terminate the simulation, either gracefully or with force. The executable understand the following signals:

- SIGINT (`CTRL+C`):
  Request a graceful shutdown of the simulation. This means the currently processed events are finished, while events
  placed on the buffer as well as all additionally requested events from the configuration file are ignored. After
  finishing the current events, the finalization stage is run for every module to ensure that the simulation terminates
  properly. This signal can be very useful when too many events are specified and the simulation takes too long to finish
  entirely, but the output generated so far should still be kept.

- SIGTERM:
  Same as SIGINT, request a graceful shutdown of the simulation. This signal is emitted e.g. by the `kill` command or by
  cluster computing schedulers to ask for a termination of the job.

- SIGQUIT (`CTRL+\`):
  Forcefully terminates the simulation. It is not recommended to use this signal as it will normally lead to the loss of
  all generated data. This signal should only be used when graceful termination is for any reason not possible.

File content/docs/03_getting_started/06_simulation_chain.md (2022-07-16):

---
# SPDX-FileCopyrightText: 2022 CERN and the Allpix Squared authors
# SPDX-License-Identifier: CC-BY-4.0
title: "Setting up the Simulation Chain"
weight: 6
---

In the following, the framework parameters are used to set up a fully functional simulation. Module parameters are shortly
introduced when they are first used. For more details about the module parameters, the respective module documentation in
[Chapter 7](../../07_modules) should be consulted. A typical simulation in Allpix Squared will contain the following
components:

- The **geometry builder**, responsible for creating the external Geant4 geometry from the internal geometry. In this
  document, *internal geometry* refers to the detector parameters used by Allpix Squared for coordinate transformations and
  conversions throughout the simulation, while *external geometry* refers to the constructed Geant4 geometry used for
  charge carrier deposition (and possibly visualization).

- The **deposition** module that simulates the particle beam creating charge carriers in the detectors using the provided
  physics list (containing a description of the simulated interactions) and the geometry created above.

- A **propagation** module that propagates the charges through the sensor.

- A **transfer** module that transfers the charges from the sensor electrodes and assigns them to a pixel of the readout
  electronics.

- A **digitizer** module which converts the charges in the pixel to a detector hit, simulating the front-end electronics
  response.

- An **output** module, saving the data of the simulation. The Allpix Squared standard file format is a ROOT `TTree`, which
  is described in detail in [Section 4.7](.././09_storing_output_data).

In this example, charge carriers will be deposited in the three sensors defined in the detector configuration file from
[Section 3.3](.././03_detector_configuration). All charge carriers deposited in the different sensors will be propagated and
digitized. Finally, monitoring histograms for the device under test (DUT) will be recorded in the framework's main ROOT file
and all simulated objects, including the entry and exit positions of the simulated particles (Monte Carlo truth), will be
stored in a ROOT file using the Allpix Squared format. An example configuration file implementing this would look like:

```ini
# Global configuration
[Allpix]
# Simulate a total of 5 events
number_of_events = 5
# Use the short logging format
log_format = "SHORT"
# Location of the detector configuration
detectors_file = "manual_detector.conf"

# Read and instantiate the detectors and construct the Geant4 geometry
[GeometryBuilderGeant4]

# Initialize physics list and particle source
[DepositionGeant4]
# Use a Geant4 physics lists with EMPhysicsStandard_option3 enabled
physics_list = FTFP_BERT_LIV
# Use a charged pion as particle
particle_type = "pi+"
# Set the energy of the particle
source_energy = 120GeV
# Origin of the beam
source_position = 0 0 -12mm
# The direction of the beam
beam_direction = 0 0 1
# Use a single particle in a single event
number_of_particles = 1

# Propagate the charge carriers through the sensor
[GenericPropagation]
# Set the temperature of the sensor
temperature = 293K
# Propagate multiple charges at once
charge_per_step = 50

# Transfer the propagated charges to the pixels
[SimpleTransfer]
max_depth_distance = 5um

# Digitize the propagated charges
[DefaultDigitizer]
# Noise added by the readout electronics
electronics_noise = 110e
# Threshold for a hit to be detected
threshold = 600e
# Threshold dispersion
threshold_smearing = 30e
# Noise added by the digitisation
qdc_smearing = 100e

# Save histograms to the ROOT output file
[DetectorHistogrammer]
# Save histograms for the "dut" detector only
name = "dut"

# Store all simulated objects to a ROOT file with TTrees
[ROOTObjectWriter]
# File name of the output file
file_name = "allpix-squared-output"
# Ignore initially deposited charges and propagated carriers:
exclude = DepositedCharge, PropagatedCharge
```

This configuration is available in the repository \[[@ap2-repo]\] at `etc/manual.conf`. The detector configuration file can
be found at `etc/manual_detector.conf`.

The simulation is started by passing the path of the main configuration file to the `allpix` executable as follows:

```sh
allpix -c etc/manual.conf
```

The detector histograms such as the hit map are stored in the ROOT file `output/modules.root` in the TDirectory
`DetectorHistogrammer/`.

If problems occur when exercising this example, it should be made sure that an up-to-date and properly installed version of
Allpix Squared is used (see the installation instructions in [Chapter 2](../../02_installation)). If modules or models
fail to load, more information about potential issues with the library loading can be found in the detailed framework
description in [Section 4.4](../../04_framework/04_modules#module-instantiation).

[@ap2-repo]: https://gitlab.cern.ch/allpix-squared/allpix-squared

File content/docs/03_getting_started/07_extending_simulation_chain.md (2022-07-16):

---
# SPDX-FileCopyrightText: 2022 CERN and the Allpix Squared authors
# SPDX-License-Identifier: CC-BY-4.0
title: "Extending the Simulation Chain"
weight: 7
---

In the following, a few basic modules will be discussed which may be of use during a first simulation.

## Visualization

Displaying the geometry and the particle tracks helps both in checking and interpreting the results of a simulation.
Visualization is fully supported through Geant4, supporting all the options provided by Geant4 \[[@geant4vis]\]. Using the Qt
viewer with OpenGL driver is the recommended option as long as the installed version of Geant4 is built with Qt support
enabled.

To add the visualization, the `VisualizationGeant4` section should be added at the end of the configuration file. An example
configuration with some useful parameters is given below:

```ini
[VisualizationGeant4]
# Use the Qt gui
mode = "gui"

# Set transparency of the detector models (in percent)
transparency = 0.4
# Set viewing style (alternative is 'wireframe')
view_style = "surface"

# Color trajectories by charge of the particle
trajectories_color_mode = "charge"
trajectories_color_positive = "blue"
trajectories_color_neutral = "green"
trajectories_color_negative = "red"
```

If Qt is not available, a VRML viewer can be used as an alternative, however it is recommended to reinstall Geant4 with the
Qt viewer included as it offers the best visualization capabilities. The following steps are necessary in order to use a VRML
viewer:

- A VRML viewer should be installed on the operating system. Good options are FreeWRL or OpenVRML.

- Subsequently, two environmental parameters have to be exported to the shell environment to inform Geant4 about the
  configuration: `G4VRMLFILE_VIEWER` should point to the location of the viewer executable and should
  `G4VRMLFILE_MAX_FILE_NUM` typically be set to 1 to prevent too many files from being created.

- Finally, the configuration section of the visualization module should be altered as follows:
  ```ini
  [VisualizationGeant4]
  # Do not start the Qt gui
  mode = "none"
  # Use the VRML driver
  driver = "VRML2FILE"
    ```

More information about all possible configuration parameters can be found in the
[`VisualizationGeant4` documentation](../../07_modules/visualizationgeant4).

## Electric Fields

By default, detectors do not have an electric field associated with them, and no bias voltage is applied. A field can be
added to each detector using the `ElectricFieldReader` module.

The section below calculates a linear electric field for every point in active sensor volume based on the depletion voltage
of the sensor and the applied bias voltage. The sensor is always depleted from the implant side. The direction of the
electric field depends on the sign of the bias voltage as described in the
[`ElectricFieldReader documentation](../../07_modules/electricfieldreader).

```ini
# Add an electric field
[ElectricFieldReader]
# Set the field type to `linear`
model = "linear"
# Applied bias voltage to calculate the electric field from
bias_voltage = -50V
# Depletion voltage at which the given sensor is fully depleted
depletion_voltage = -10V
```

Allpix Squared also provides the possibility to utilize a full electrostatic TCAD simulation for the description of the
electric field. In order to speed up the lookup of the electric field values at different positions in the sensor, the
adaptive TCAD mesh has to be interpolated and transformed into a regular grid with configurable feature size before use.
Allpix Squared comes with a converter tool which reads TCAD DF-ISE files from the sensor simulation, interpolates the field,
and writes this out in an appropriate format. A more detailed description of the tool can be found in
[Section 13.2](../../13_additional/mesh_converter). An example electric field can be found in the repository \[[@ap2-repo]\]
at `etc/example_electric_field.init`.

Electric fields can be attached to a specific detector using the
standard syntax for detector binding. A possible configuration would be:

```ini
[ElectricFieldReader]
# Bind the electric field to the detector named `dut`
name = "dut"
# Specify that the model is provided as meshed electric field map format, e.g. converted from TCAD
model = "mesh"
# Name of the file containing the electric field
file_name = "example_electric_field.init"
```

## Magnetic Fields

For simulating the detector response in the presence of a magnetic field with Allpix Squared, a constant, global magnetic
field can be defined. By default, it is turned off. A field can be added to the whole setup using the unique module
`MagneticFieldReader`, passing the field vector as parameter:

```ini
# Add a magnetic field
[MagneticFieldReader]
# Constant magnetic field (currently this is the default value)
model = "constant"
# Magnetic field vector
magnetic_field = 0mT 3.8T 0T
```

The global magnetic field is used by the interface to Geant4 and therefore exposes charged primary particles to the Lorentz
force, and as a property of each detector present, enabling a Lorentz drift of the charge carriers in the active sensors, if
supported by the used propagation modules. See the [Chapter 7](../../07_modules) for more information on the available
propagation modules.

Currently, only constant magnetic fields can be applied. For all parameters, refer to the
[`MagneticFieldReader` documentation](../../07_modules/magneticfieldreader).

[@geant4vis]: https://geant4.web.cern.ch/geant4/UserDocumentation/UsersGuides/ForApplicationDeveloper/html/ch08.html
[@ap2-repo]: https://gitlab.cern.ch/allpix-squared/allpix-squared

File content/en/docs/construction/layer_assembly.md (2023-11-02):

---
# SPDX-FileCopyrightText: 2022 100µPET
# SPDX-License-Identifier: CC-BY-4.0
title: "Layer assembly"
weight: 1
---

The scanner assembly starts with the integration of 4 detectors ASICs into a Flexible-Printed-Circuit (FPC), creating a scanner's layer module, in a 2x2 arrangement with 300 µm gap between chip edges.



- The assembly of the layer module consists in loading the 4 detector ASICs and the FPC into their respective parts of an assembly jig. 
    - The electromechanical bonding glue (NCP), Huntsman Araldite 2011, is dispensed in the flex using a stencil.
- The two parts will be brought into proximity using alignment pins and micropositioners. 
    - The alignemnt between the chips and the flex will be done using metalic fiducial marks in the FPC and the ASICs silicon edges. 
    - The alignemt is done via the micropositioners through inspection holes in the assembly jig and FPC. 
- Thermocompression will be applied to bond the chips to the flex. 
    - 20 kgf bonding force was tested successfully with NCP, with 100% connection yield and no deterioration during and after stress current test

The bonding qualification tests were done with:
- Contact resistance measurements (2-wires of full chain)
- High current injection tests, up to 200 mA\*, before and after thermal cycles.
</br>
\*6-10x more than what is expected per bonding pad on final ASIC)
- Thermal cycles from 5 to 60°C.

This allowed us to understand a number of facts and fine tuning the bonding process:
- Bonding technique was fined tuned with a preheating step at 60°C in order to reduce the glue viscosity before applying the nominal compression force.
    - Need of such bonding step in final assembly is **TBC**
- Thermal cycles shown that mechanical reinforcement at the chip corners is important. Therefore, in addition to the horizontal glue lines dispensed over the pad rows, two vertical lines are doposited at the end of each row.
    - The contact resistance of the chain, when bonded with Higher forces (as 50 kgf for example) is less sensitive to the temperature cycles, while the 20 kgf contact got worse after the cycles.
        - When the temperature cycles were performed on a dry enviroment, the samples bonded with 20 kgf did not show any deterioration.



### Specs **TODO**
- Assembly qualification with home-made tools with heating and compression system. Design to be made by Franck with inputs from Coralie and Didier and with inputs from the flex and chip features/dimensions.  

### Chips placement
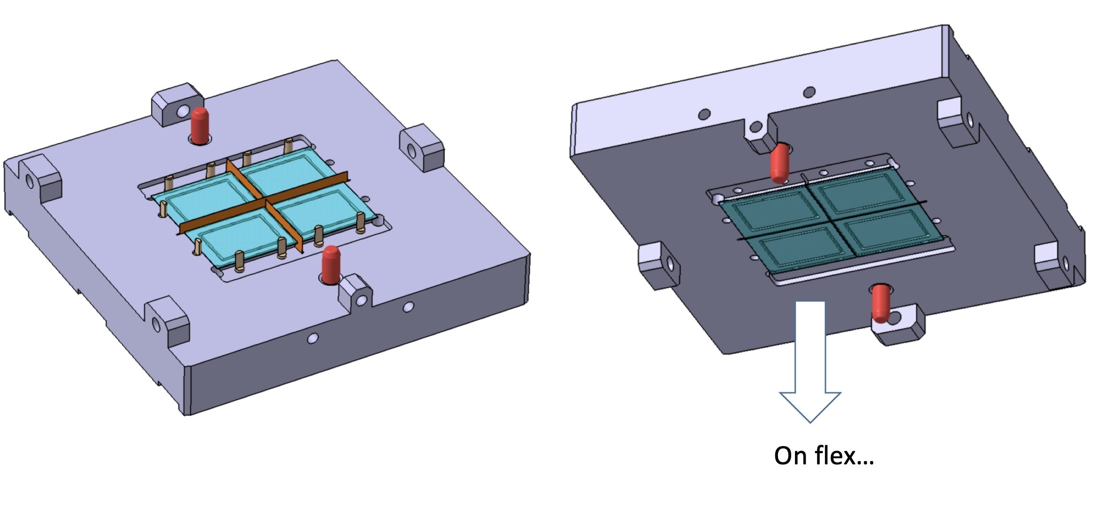
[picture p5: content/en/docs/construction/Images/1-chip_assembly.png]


### Flex placement
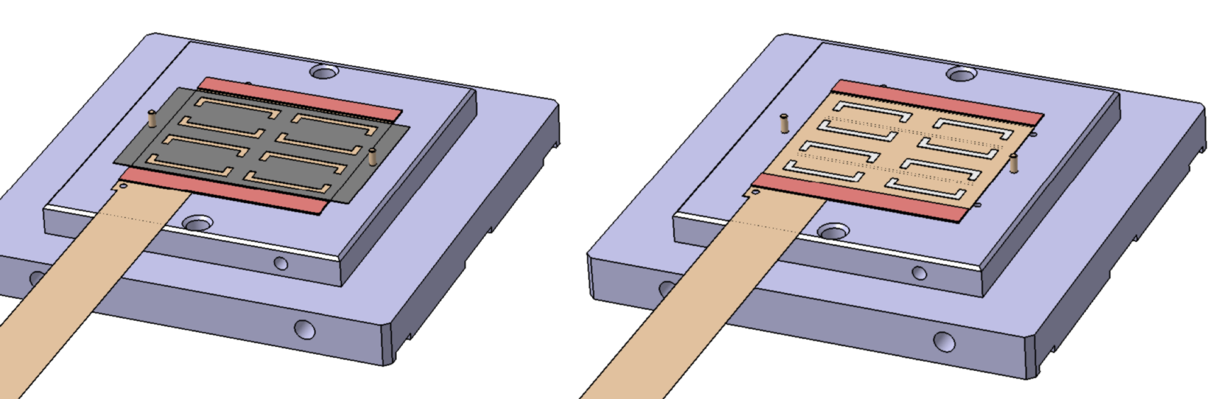
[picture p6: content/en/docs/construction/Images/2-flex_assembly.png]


### Jigs contact
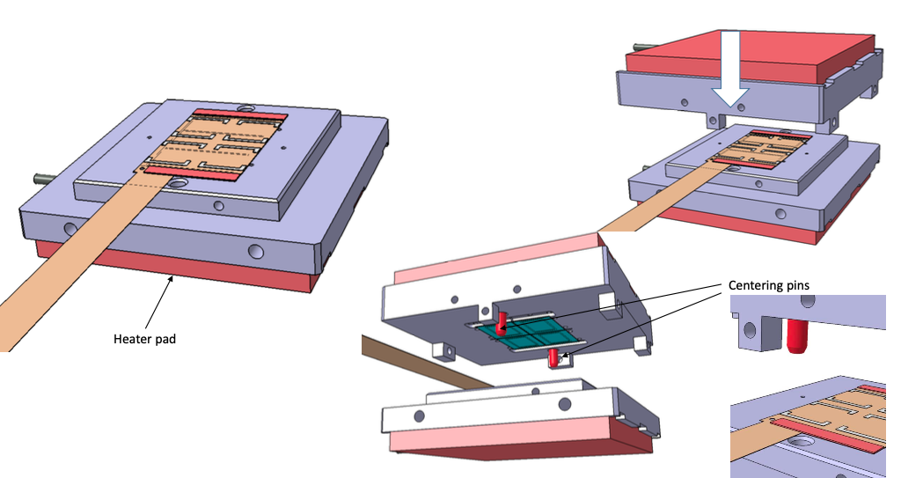
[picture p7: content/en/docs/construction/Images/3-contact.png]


### Fine-alignment
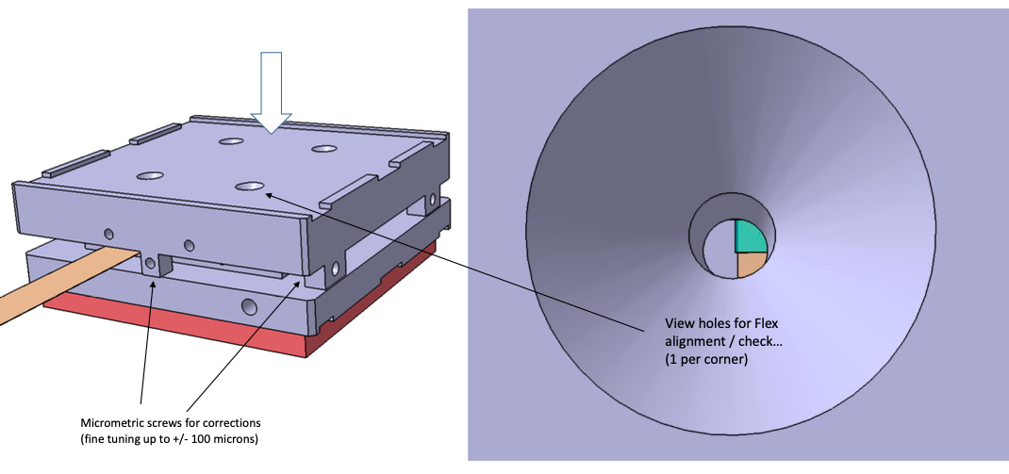
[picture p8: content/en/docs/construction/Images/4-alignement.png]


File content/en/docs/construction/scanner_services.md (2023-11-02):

---
# SPDX-FileCopyrightText: 2022 100µPET
# SPDX-License-Identifier: CC-BY-4.0
title: "Scanner services"
weight: 4
---

The scanner has a total of 960 chips. They are assembled in 240 modules (4 chips each) that are further grouped into double-layer modules (8 chips) via the TMI board.
- The ASIC has a 3-bit address. Is it worth to daisy-chain two layers and consider it one element for servicing?

## Specs **TODO**
- Total power (voltage and current levels)  needed for a double-layer module and full tower with 30 double-layer modules
    - Calculated amount of power supplies needed
- Estimate needed cooling power and performance for latest design

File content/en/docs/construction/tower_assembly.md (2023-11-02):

---
# SPDX-FileCopyrightText: 2022 100µPET
# SPDX-License-Identifier: CC-BY-4.0
title: "Tower assembly"
weight: 2
---

The assembly of the scanner's tower consists in mounting the previously assembled layer modules into a stack.
60 layers will compose the tower, and such tower will be encapsulated by the cooling housing.

The modules will be stacked using alignment pins to constrain the relative position betwen layers.



### Specs **TODO**
- Will consective modules, or the double-layer modules, have adhesive between? Are the layers replacable if needed?
    - This will add the adhesive thickness (x60) to the total height of the tower

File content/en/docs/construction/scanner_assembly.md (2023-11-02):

---
# SPDX-FileCopyrightText: 2022 100µPET
# SPDX-License-Identifier: CC-BY-4.0
title: "Scanner assembly"
weight: 3
---

The assembly of the scanner is the positioning of the 4 towers with respect with each other.

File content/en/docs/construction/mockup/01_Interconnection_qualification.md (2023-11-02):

---
# SPDX-FileCopyrightText: 2022 100µPET
# SPDX-License-Identifier: CC-BY-4.0
title: "Test-chip"
weight: 1
---

The scanner prototype will use test-chips to validate the simultaneous bonding of multiple chips, the stacking of the layer modules, and the cooling performance.
The test-chip is designed on top of the original 100µPET ASIC layout, using its pads in the top metal layer and passivation openings to connect structures arranged in the chip. Therefore, it is intended to be identical to the final ASIC in terms of dimensions and interface.

## Test-chip details

In addition to a few chain segments for bonding continuity tests, will also have a 4-wire probing points to measure the single bond resistance, a spiral heater in the center of the chip, and two PT-XYZ-like RTD (Resistive Temperature Detector). Au stud bumps will be deposited on all bonding pads for flip-chip connection with test-FPC. The test-chip will be produced on 300 µm thick Si wafers (4-inch) and will have a Ti/Pt/Ti/Al stack (3-10 µm Ti, 100 nm Pt and 300 nm Al). 

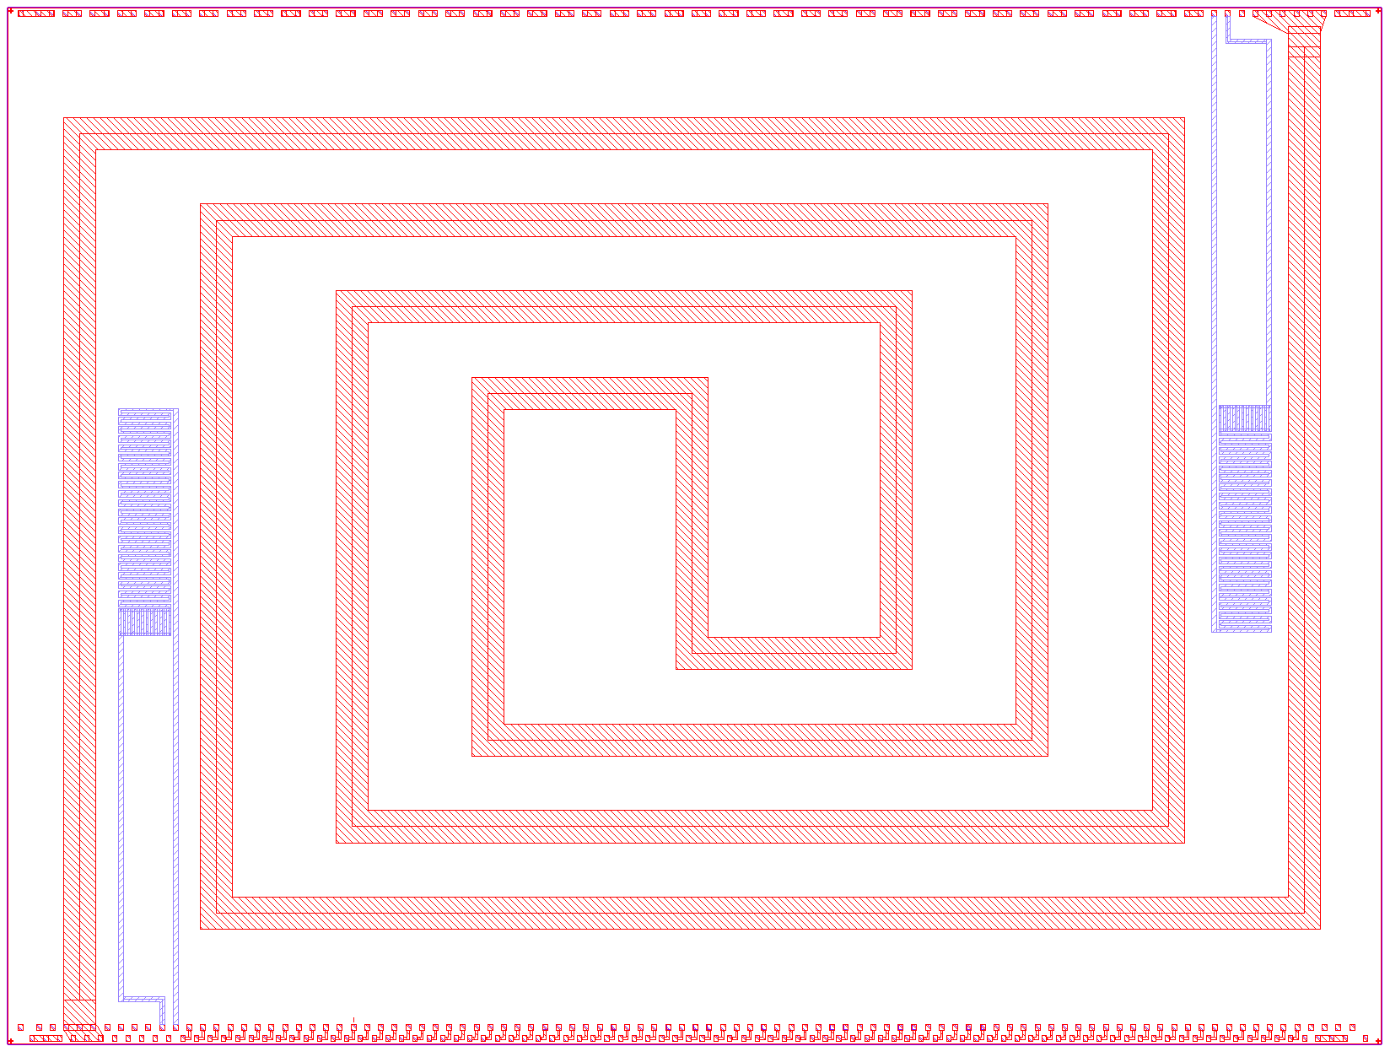
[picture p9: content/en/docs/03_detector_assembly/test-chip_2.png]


### Heater
The picture above shows the layout of the test-chip. The large spiral in the center is made of Ti/Al with a total length of approximately 24 cm. 6 Au stud bumps on each end of the line connects it to a voltage source to dissipate 1 W of power (as a working scanner chip). With a trace width of 704.6 µm, the wire resistance results in 27 Ohms (at 0 degC, using 2.7 µOhm.cm for the Al resistivity and 0.0043 for temperature coeficient alpha). The estimated current going through the trace is about 200 mA.

<div style="display: flex;
            justify-content: space-between;
            align-items: flex-start;">
   <div style="text-align: center;
            flex: 0 0 45%; /* Adjust the width as needed */
            margin: 10px;">
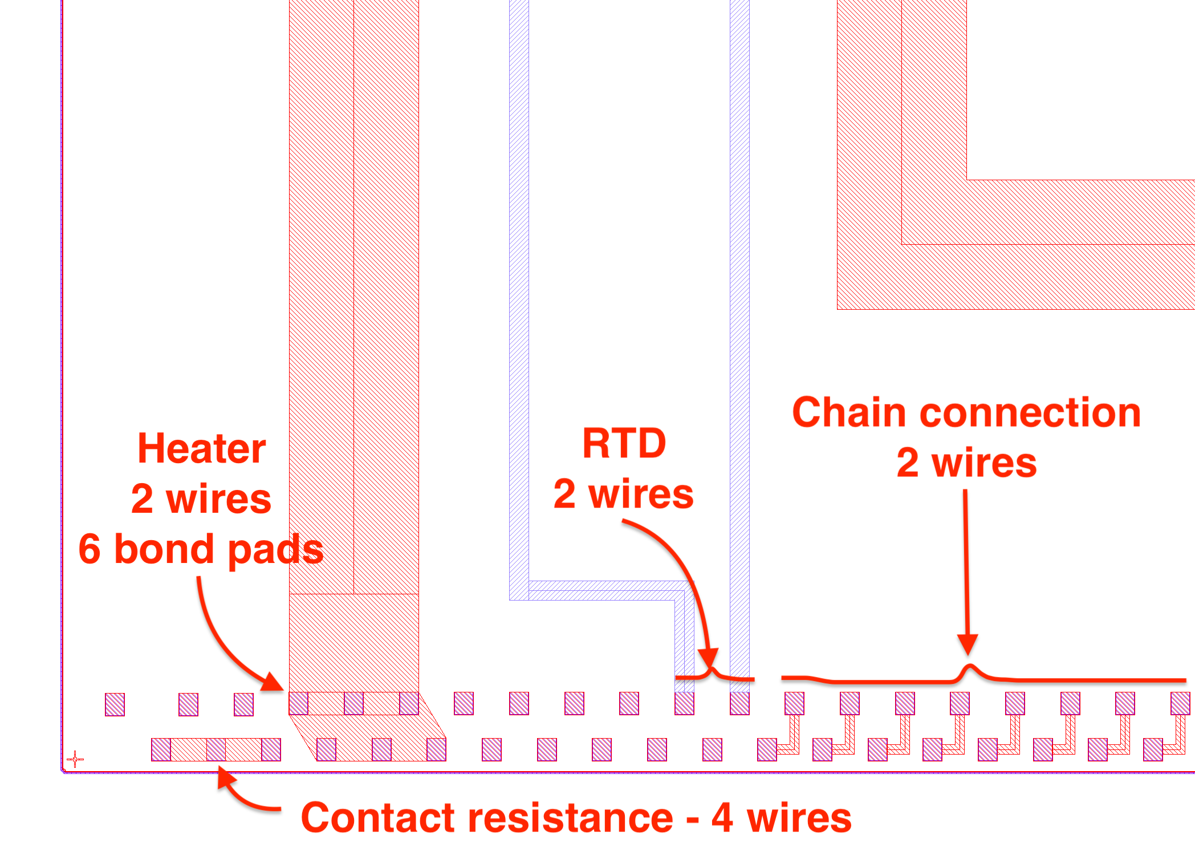
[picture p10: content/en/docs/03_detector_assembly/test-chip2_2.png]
        
        <div style="margin-top: 5px;
            font-size: 14px;
            text-align: center;">Bottom left corner</div>
    </div>
   <div style="text-align: center;
            flex: 0 0 45%; /* Adjust the width as needed */
            margin: 10px;">
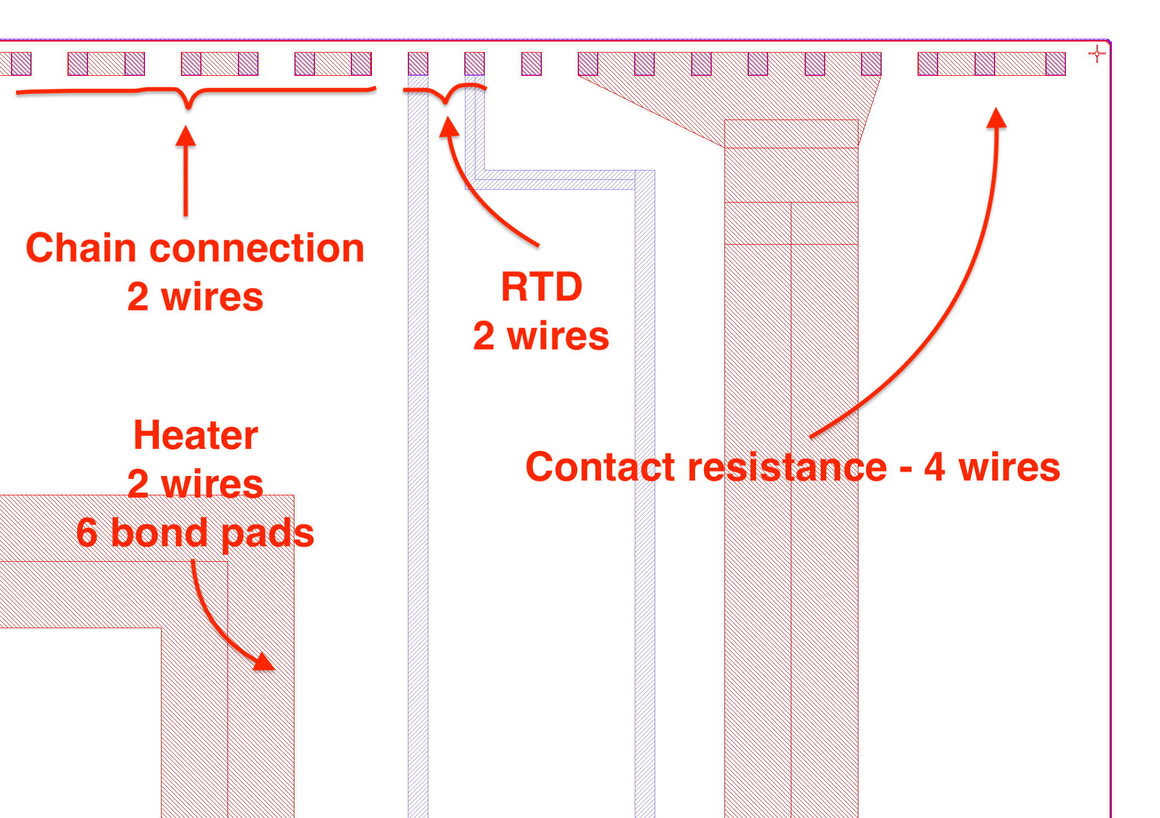
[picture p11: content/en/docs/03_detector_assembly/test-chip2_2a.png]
        
        <div style="margin-top: 5px;
            font-size: 14px;
            text-align: center;">Top right corner</div>
    </div>
</div>

### Resistive Temperature Detector
The PT-XYZ RTD is the small ladder-and-snake pattern and is made of Ti/Pt. With 100 nm thick Pt, 50 µm wide traces and about 54 mm length, using 10.6 µOhm.cm for Pt resistivity, we have 1033 Ohms at 0 degC for the total resistance of the RTD.

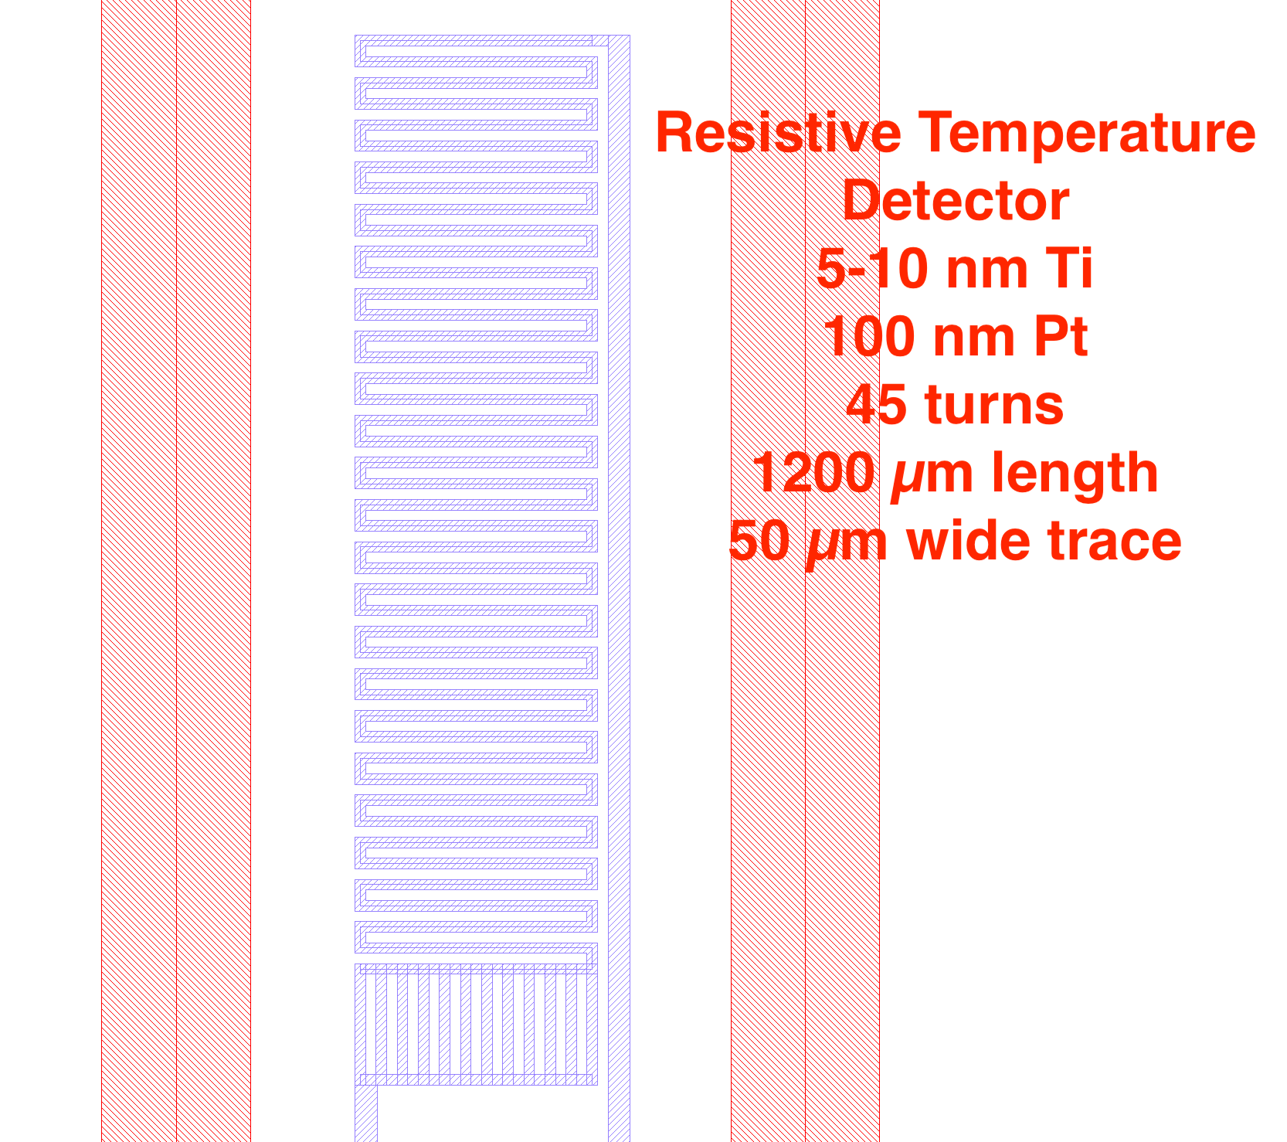
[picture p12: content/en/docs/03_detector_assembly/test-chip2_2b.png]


### Contact resistance measurement
There are groups of 3 pads that are shorted together via the Ti/Al layer. These are intended to be probed with 4-wires as described in the image bellow (from Flip Chip Technologies by John H. Lau), allowing to measure the contact resistance of a single bond. These groups are 3 pads conected are placed in the 4 edges of the chip, as well as in the center of it.

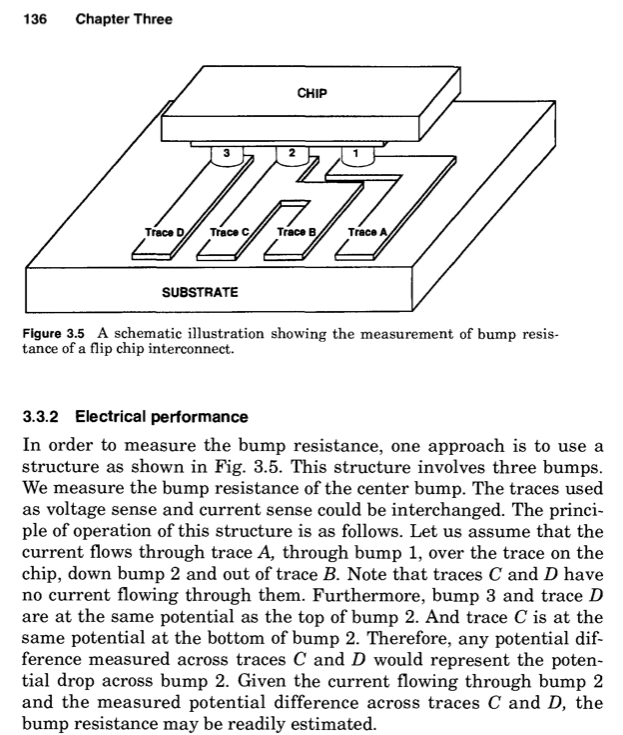
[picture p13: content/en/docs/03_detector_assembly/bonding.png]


### Chains
<br>Finally, the last structures on the test-chip are the chain links designed to close a complete chain when bonded to the test-FPC. These are intended to be used for stress tests of the bonding by injecting some high currents (DC up to 200 mA).

Considering that the final ASICs on the final FPC will have some signals that are shared among the other ASICs, while some other signals are connected in a chain through the chips, the relative orientation of the chips on the flex will have a large impact in routing the many power and signal lines through the FPC. It is important to note that the performance of the scanner is impacted by the thickness of the FPC (and hance how many layers are used), and a thinner FPC is preferrable.

## Test-chip size

The test-chip is designed using the original 100µPET ASIC design (using the top metal and passivation layout), and its position on the test-wafer follows the same positioning as the final 100µPET wafer, with 100 µm of silicon margin between devices. </br> 
<div style="display: flex; justify-content: space-between; align-items: flex-start;">
   <div style="text-align: center; flex: 0 0 45%; margin: 0px;">
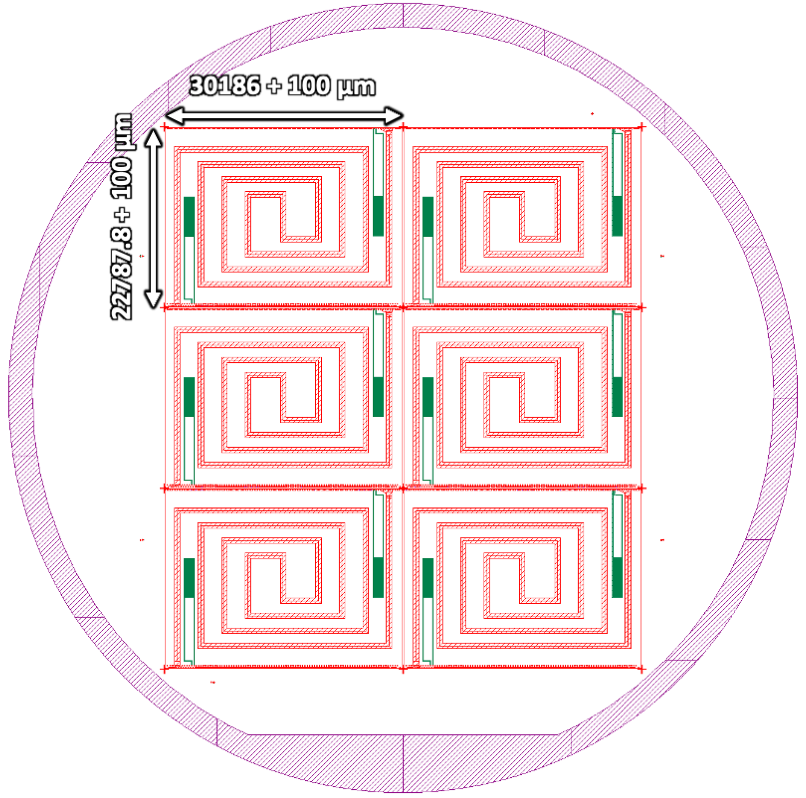
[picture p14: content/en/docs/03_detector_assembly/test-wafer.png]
   		
   		<div style="margin-top: 5px; font-size: 14px; text-align: center;">
			4-inch wafer layout with 6 test-chips
   		</div>
   </div>
   <div style="text-align: center; flex: 0 0 45%; margin: 0px; margin-right: 200px;">
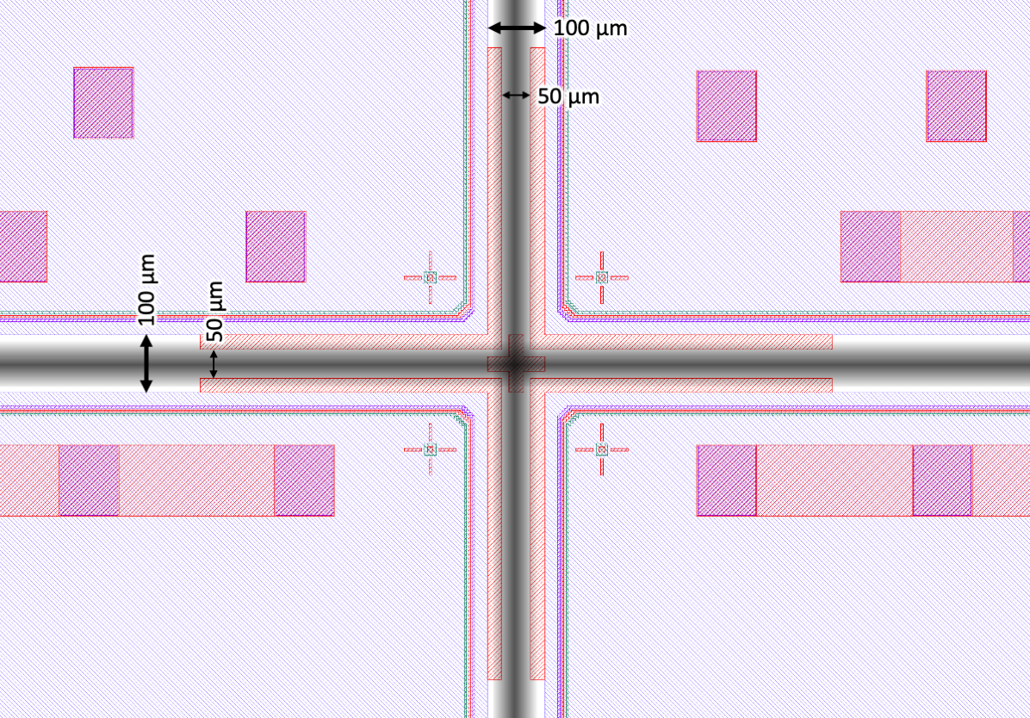
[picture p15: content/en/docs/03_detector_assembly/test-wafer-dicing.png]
   		
   		<div style="margin-top: 5px; font-size: 14px; text-align: center;">
			Zoom in the dicing street region
  		</div>
   </div>
</div>

Therefore, as discussed in the *ASIC specifications -> ASIC size* section, the size of the test-chip after dicing is expected to be 22887.8 µm x 30286 µm **minus the cut-width** (illustrated as the black shaded bands in the right picture above).

From our experience using the Femto second laser available at FCBG-NMP, the street reduction due to the cut width is < 50 µm, with no visible change (i.e. up to 10 µm) along the diced edge. A few pictures below illustrates the chip after dicing.

<div style="display: flex; justify-content: space-between; align-items: flex-start;">
   <div style="text-align: center; flex: 0 0 30%; margin: 0px;">
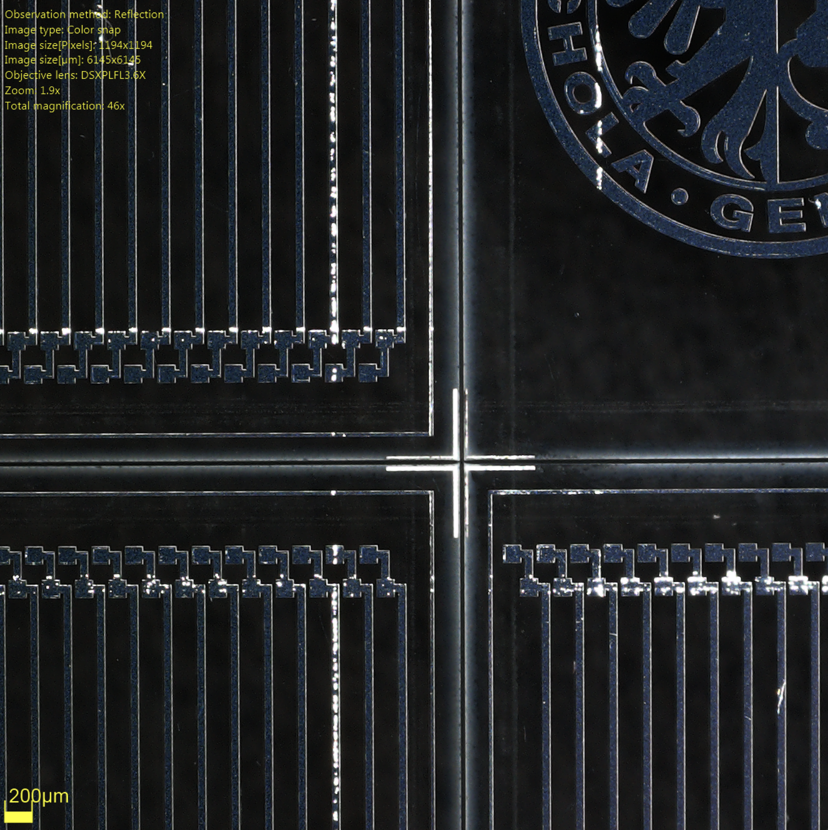
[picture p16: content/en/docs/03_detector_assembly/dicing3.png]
   		
   		<div style="margin-top: 5px; font-size: 14px; text-align: center;">
			Diced wafer
   		</div>
   </div>
   <div style="text-align: center; flex: 0 0 30%; margin: 0px;">
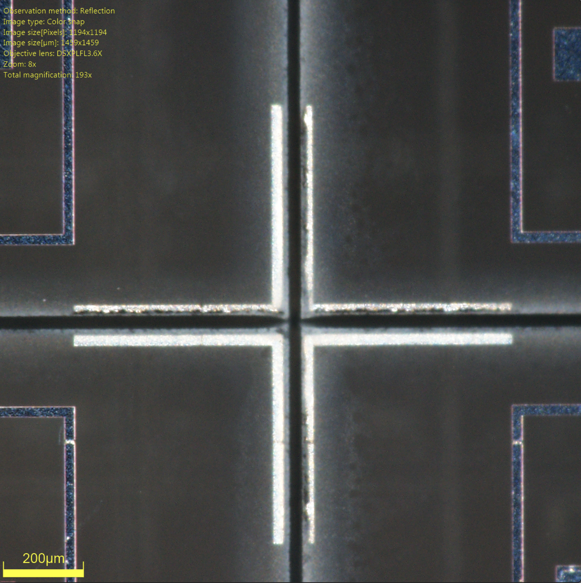
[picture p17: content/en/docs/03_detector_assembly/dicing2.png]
   		
   		<div style="margin-top: 5px; font-size: 14px; text-align: center;">
			Zoom in dice mark between chips 
  		</div>
   </div>
   <div style="text-align: center; flex: 0 0 30%; margin: 0px;">
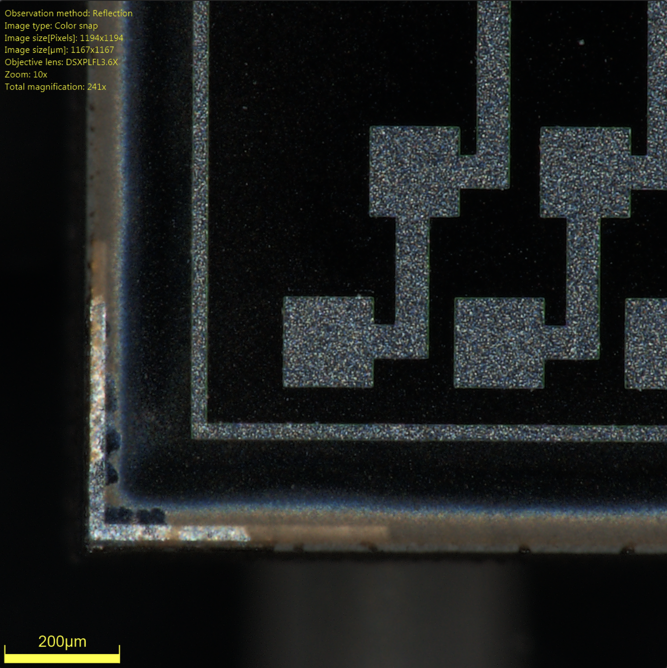
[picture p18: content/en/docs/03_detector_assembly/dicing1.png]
   		
   		<div style="margin-top: 5px; font-size: 14px; text-align: center;">
			Test-chip after dicing
  		</div>
   </div>
</div></br>

Therefore, the expected dimensions of the 100µPET test-chip, after dicing, is **22837.8 µm x 30236 µm**.

### Test-wafer alignment marks
The process flow for the production of our test-wafer will be uploaded soon. 
There are 6 alignment marks over the wafer, as shown in the image below, that are used to align the multiple photolitography steps between each other.

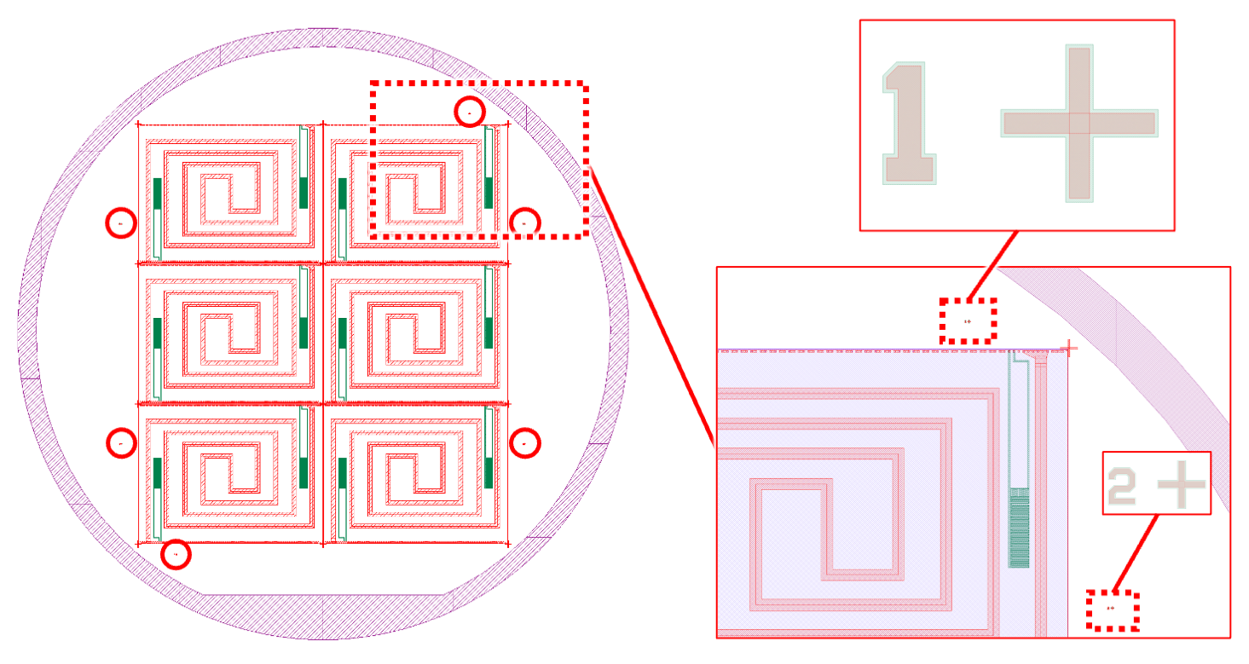
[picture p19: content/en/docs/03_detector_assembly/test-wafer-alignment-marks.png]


The positons of the marks in absolute coordinates, having (0,0) in the center of the wafer, are:

| # Alignment mark | X [µm] | Y [µm] |
|:-----------------|:-------|:-------|
| 1                | 24000  | 36000  |
| 2                | 33000  | 18000  |
| 3                | 33000  | -18000 |
| 4                | -24000 | -36000 |
| 5                | -33000 | -18000 |
| 6                | -33000 | 18000  |
## Production process flow
The process flow for wafer production at FCBG-NMP is avalable below.
<object data="../100uPET_MVicente_NMP_Process_Flow.pdf" type="application/pdf" width="100%" height="510px"></object>

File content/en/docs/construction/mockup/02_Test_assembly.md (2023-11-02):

---
# SPDX-FileCopyrightText: 2022 100µPET
# SPDX-License-Identifier: CC-BY-4.0
title: "Test assembly"
weight: 2
---

## ASIC orientation
Some possible options for the orientation of the chips is shown in the image below.
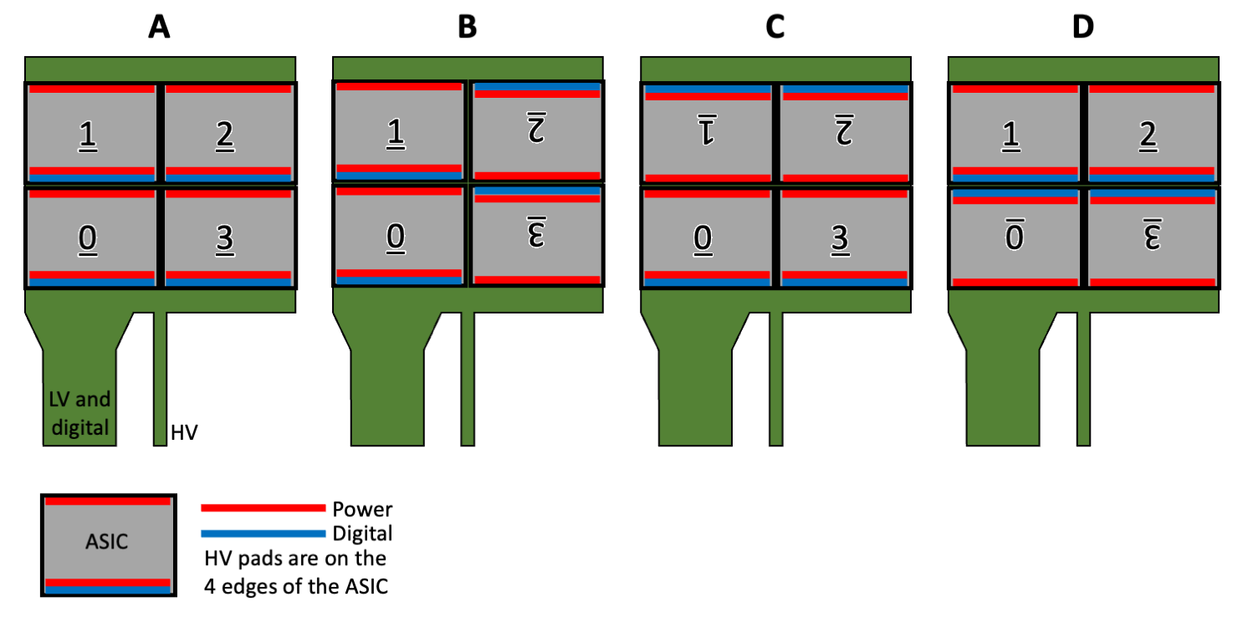
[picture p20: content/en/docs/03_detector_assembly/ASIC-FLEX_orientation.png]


In option **A** all chips have the same orientation ((digital) periphery to bottom).
<br>Option **B** has chips #2 and #3 rotated 180 degrees, possibily easing the connetcion between chips #1 and #2 of the signals in chain.
<br>Option **C** has chips #1 and #2 rotated 180 degrees, so all chips has their digital periphery closer to the top/bottom edges of the FPC, where decoupling capacitors and other passive components of the FPC are hosted.
<br>Option **D** is the oposite as option C, having the digital periphery of all chips the furthest from the decoupling capacitors but offering the shortest distance for the chip-to-chip signals.

As the chips has the HV connection pads in all of their 4 edges, independent of the chip's orientation it will be always possible to have the HV line routed from the HV tail towards the center of the flex, allowing to HV bias all 4 chips with the shortest path.

## Test-chip wiring
The test assembly of the 4 test-chips on the test-flex will connect a few functionalities of each chip, as illustrated below.



While the total amount of wires to route is 46, only two wires are used to control all the heaters as they are daisy chained in the flex. Threfore, the amount of wires going to the flex tail and to the ZIF connector is 40. The ZIF connector to be used is the <a href="https://www.hirose.com/product/series/FH41">Hirose FH41 series</a> with 40 positions

### Test-structure pads
Considering the 100µPET final ASIC IO pad numbering, the structures on the test-schip are connected to the following pads.

| Test structure                    | #Pads                          |
|:----------------------------------|:-------------------------------|
| Bottom left CR                    | 2, 4\*, 6                      |
| Bottom right CR                   | 190, 192\*, 194                |
| Top left CR                       | 197, 198\*, 199                  |
| Top right CR                      | 293, 294\*, 295                  |
| Heater +                          | 7, 8, 9, 10, 11, 12            |
| Heater -                          | 287, 288, 289, 290, 291, 292   |
| Left RTD                          | 21 (+), 23 (-)                 |
| Right RTD                         | 284 (+), 285 (-)               |
| Bottom chain                      | 24 (+), 188 (-)                |
| Top chain                         | 200 (+), 283 (-)               |

\*Pads #4 #192 #198 and #294 should each be connected to 2 wires for a 4-wires measurement.

### Dummy SMD components 
TODO, describe SMD capacitors mouning on dummy pads for ptotoyping the stacking of the layers.

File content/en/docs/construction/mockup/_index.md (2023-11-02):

---
# SPDX-FileCopyrightText: 2022 100µPET
# SPDX-License-Identifier: CC-BY-4.0
title: "Scanner Mockup"
description: "Scanner prototyping plans for design and assembly evalutaion"
weight: 6
---

The design and assembly of the scanner will be prototyped with a dedicated test-chip to be produced at FCBG-NMP.
There will be 40 300µm thick Si wafers produced, each containing 6 test-chips (described in the next section).

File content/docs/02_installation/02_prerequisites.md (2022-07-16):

---
# SPDX-FileCopyrightText: 2022 CERN and the Allpix Squared authors
# SPDX-License-Identifier: CC-BY-4.0
title: "Prerequisites"
weight: 2
---

If the framework is to be compiled and executed on CERN's LXPLUS service, all build dependencies can be loaded automatically
from the CVMFS ﬁle system.

The core framework is compiled separately from the individual modules and Allpix Squared has therefore only two required
external dependencies:

- ROOT 6 \[[@root]\]:
  ROOT is used for histogramming as well as coordinate transformations. In addition, some modules implement I/O using ROOT
  libraries. The latest stable release of ROOT 6 is recommended and older versions, such as ROOT 5.x, are not supported.
  Please refer to \[[@rootinstallation]\] for instructions on how to install ROOT. ROOT has several components of which the
  `GenVector` package is required to run Allpix Squared. This package is included in the default build. ROOT needs to be
  built using C++17, which is accomplished by supplying the CMake flag `-DCMAKE_CXX_STANDARD=17`.

- Boost.Random 1.64.0 or later \[[@boostrandom]\]:
  Random number generator and distribution library of the Boost project, used in order to get cross-platform portable,
  STL-compatible random number distributions. While STL random number generators are portable and guarantee to deliver the
  same random number sequence given the same seed, random distributions are not, and their implementation is
  platform-dependent leading to different simulation results with the same seed. Since the implementation of some random
  distributions (most notably of `boost::normal_distribution`) has changed in the past, a recent version is required.

For some modules, additional dependencies exist. For details about the dependencies and their installation see
[Chapter 7](../../07_modules). The following dependencies are needed to compile the standard installation:

- Geant4 \[[@geant4]\]:
  Simulates the desired particles and their interactions with matter, depositing charges in the detectors with the help of
  the constructed geometry. See the instructions in \[[@geant4installation]\] for details on how to install the software.
  All Geant4 data sets are required to run the modules successfully, and Geant4 must be built using C++17. For
  multithreading to be possible, this must also be enabled in the Geant4 installation. It is recommended to enable the
  Geant4 Qt extensions to allow visualization of the detector setup and the simulated particle tracks. A recommended set of
  CMake flags to build a Geant4 package suitable for usage with Allpix Squared are:
  ```
  -DGEANT4_INSTALL_DATA=ON
  -DGEANT4_USE_GDML=ON
  -DGEANT4_USE_QT=ON
  -DGEANT4_USE_XM=ON
  -DGEANT4_USE_OPENGL_X11=ON
  -DGEANT4_BUILD_CXXSTD=17
  -DGEANT4_BUILD_MULTITHREADED=ON
  ```

- Eigen3 \[[@eigen3]\]:
  Vector package used to perform Runge-Kutta integration, used in some of the charge carrier propagation modules. Eigen is
  available in almost all Linux distributions through the package manager. Otherwise it can be easily installed, comprising
  a header-only library.

Extra flags need to be set for building an Allpix Squared installation without these dependencies. Details about these
configuration options are given in the [Section 2.5](.././05_cmake_configuration).

[@root]: http://root.cern.ch/
[@rootinstallation]: https://root.cern.ch/building-root
[@boostrandom]: https://www.boost.org/doc/libs/1_75_0/doc/html/boost_random/reference.html
[@geant4]: https://doi.org/10.1016/S0168-9002(03)01368-8
[@geant4installation]: https://geant4-userdoc.web.cern.ch/UsersGuides/InstallationGuide/html
[@eigen3]: http://eigen.tuxfamily.org

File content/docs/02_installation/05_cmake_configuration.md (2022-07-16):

---
# SPDX-FileCopyrightText: 2022 CERN and the Allpix Squared authors
# SPDX-License-Identifier: CC-BY-4.0
title: "Configuration via CMake"
weight: 5
---

Allpix Squared uses the CMake build system to configure, build and install the core framework as well as all modules. An
out-of-source build is recommended: this means CMake should not be directly executed in the source folder. Instead, a build
folder should be created, from which CMake should be run. For a standard build without any additional flags this implies
executing:

```sh
mkdir build
cd build
cmake ..
```

CMake can be run with several extra arguments to change the type of installation. These options can be set with `-D<option>`
(see the end of this section for an example). Currently the following options are supported:

- `CMAKE_INSTALL_PREFIX`:
  The directory to use as a prefix for installing the binaries, libraries and data. Defaults to the source directory (where
  the folders `bin/` and `lib/` are added).

- `CMAKE_BUILD_TYPE`:
  Type of build to install, defaults to `RelWithDebInfo` (compiles with optimizations and debug symbols). Other possible
  options are `Debug` (for compiling with no optimizations, but with debug symbols and extended tracing using the Clang
  Address Sanitizer library) and `Release` (for compiling with full optimizations and no debug symbols).

- `MODEL_DIRECTORY`:
  Directory to install the internal models to. Defaults to not installing if the `CMAKE_INSTALL_PREFIX` is set to the
  directory containing the sources (the default). Otherwise the default value is equal to the directory
  `<CMAKE_INSTALL_PREFIX>/share/allpix/`. The install directory is automatically added to the model search path used by the
  geometry model parsers to find all of the detector models.

- `BUILD_TOOLS`:
  Enable or disable the compilation of additional tools such as the mesh converter. Defaults to `ON`.

- `BUILD_<ModuleName>`:
  If the specific module should be installed or not. Defaults to `ON` for most modules, however some modules with large
  additional dependencies such as LCIO \[[@lcio]\] are disabled by default. This set of parameters allows to configure the
  build for minimal requirements.

- `BUILD_ALL_MODULES`:
  Build all included modules, defaulting to `OFF`. This overwrites any selection using the parameters described above.

An example of a custom debug build, without the [`GeometryBuilderGeant4` module](../../07_modules/geometrybuildergeant4) and
with installation to a custom directory is shown below:

```sh
mkdir build
cd build
cmake -DCMAKE_INSTALL_PREFIX=../install/ \
      -DCMAKE_BUILD_TYPE=DEBUG \
      -DBUILD_GeometryBuilderGeant4=OFF ..
```

[@lcio]: https://doi.org/10.1109/NSSMIC.2012.6551478

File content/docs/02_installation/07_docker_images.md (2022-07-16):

---
# SPDX-FileCopyrightText: 2022 CERN and the Allpix Squared authors
# SPDX-License-Identifier: CC-BY-4.0
title: "Docker Images"
weight: 7
---

Docker images are provided for the framework to allow anyone to run simulations without the need of installing Allpix Squared
on their system. The only required program is the Docker executable, all other dependencies are provided within the Docker
images. In order to exchange configuration files and output data between the host system and the Docker container, a folder
from the host system should be mounted to the container's data path `/data`, which also acts as the Docker `WORKDIR`
location.

The following command creates a container from the latest Docker image in the project registry and start an interactive shell
session with the `allpix` executable already in the `$PATH`. Here, the current host system path is mounted to the `/data`
directory of the container.

```sh
docker run --interactive --tty                                   \
           --volume "$(pwd)":/data                               \
           --name=allpix-squared                                 \
           gitlab-registry.cern.ch/allpix-squared/allpix-squared \
           bash
```

Alternatively it is also possible to directly start the simulation instead of an interactive shell, e.g. using the following
command:

```sh
docker run --tty --rm                                            \
           --volume "$(pwd)":/data                               \
           --name=allpix-squared                                 \
           gitlab-registry.cern.ch/allpix-squared/allpix-squared \
           "allpix -c my_simulation.conf"
```

where a simulation described in the configuration `my_simulation.conf` is directly executed and the container terminated and
deleted after completing the simulation. This closely resembles the behavior of running Allpix Squared natively on the host
system. Of course, any additional command line arguments known to the `allpix` executable described in
[Section 3.5](../../03_getting_started/05_allpix_executable) can be appended.

For tagged versions, the tag name should be appended to the image name, e.g.
`gitlab-registry.cern.ch/allpix-squared/allpix-squared:v2.2.2`, and a full list of available Docker containers is provided
via the project's container registry \[[@ap2-container-registry]\]. A short description of how Docker images for this project
are built can be found in [Section 10.5](../../10_devtools/05_building_docker_images).

[@ap2-container-registry]: https://gitlab.cern.ch/allpix-squared/allpix-squared/container_registry

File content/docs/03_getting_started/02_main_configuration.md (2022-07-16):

---
# SPDX-FileCopyrightText: 2022 CERN and the Allpix Squared authors
# SPDX-License-Identifier: CC-BY-4.0
title: "Main Configuration"
weight: 2
---

The main configuration consists of a set of sections specifying the modules used. All modules are executed in the *linear*
order in which they are defined. There are a few section names which have a special meaning in the main configuration, namely
the following:

- The **global** (framework) header sections:
  These are all zero-length section headers (including the one at the beginning of the file) and all sections marked with
  the header `[Allpix]` (case-insensitive). These are combined and accessed together as the global configuration, which
  contain all parameters of the framework itself (see [Section 3.4](.././04_framework_parameters) for details). All
  key-value pairs defined in this section are also inherited by all individual configurations as long the key is not
  defined in the module configuration itself.

- The **ignore** header sections:
  All sections with name `[Ignore]` (case-insensitive) are ignored. Key-value pairs defined in the section as well as the
  section itself are discarded by the parser. These section headers are useful for quickly enabling and disabling
  individual modules by replacing their actual name by an ignore section header.

All other section headers are used to instantiate modules of the respective name. Installed modules are loaded automatically.
If problems arise please review the loading rules described in
[Section 4.4](../../04_framework/04_modules#module-instantiation).

Modules can be specified multiple times in the configuration files, depending on their type and configuration. The type of
the module determines how the module is instantiated:

- If the module is **unique**, it is instantiated only a single time irrespective of the number of detectors. These kinds
  of modules should only appear once in the whole configuration file unless different inputs and outputs are used, as
  explained in [Section 4.7](../../04_framework/07_module_io).

- If the module is **detector**-specific, it is instantiated once for every detector it is configured to run on. By
  default, an instantiation is created for all detectors defined in the detector configuration file
  ((see [Section 3.3](.././03_detector_configuration), lowest priority) unless one or both of the following parameters are
  specified:

  - `name`:
    An array of detector names the module should be executed for. Replaces all global and type-specific modules of the
    same kind (highest priority).

  - `type`:
    An array of detector types the module should be executed for. Instantiated after considering all detectors specified
    by the name parameter above. Replaces all global modules of the same kind (medium priority).

    Within the same module, the order of the individual instances in the configuration file is irrelevant.

A valid example configuration using the detector configuration above is:

```ini
# Key is part of the empty section and therefore the global configuration
string_value = "example1"
# The location of the detector configuration is a global parameter
detectors_file = "manual_detector.conf"
# The Allpix section is also considered global and merged with the above
[Allpix]
another_random_string = "example2"

# First run a unique module
[MyUniqueModule]
# This module takes no parameters
# [MyUniqueModule] cannot be instantiated another time

# Then run detector modules on different detectors
# First run a module on the detector of type Timepix
[MyDetectorModule]
type = "timepix"
int_value = 1
# Replace the module above for `dut` with a specialized version
# It does not inherit any parameters from earlier modules
[MyDetectorModule]
name = "dut"
int_value = 2
# Run the module on the remaining unspecified detector (`telescope1`)
[MyDetectorModule]
# int_value is not specified, so it uses the default value
```

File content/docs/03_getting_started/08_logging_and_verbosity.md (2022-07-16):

---
# SPDX-FileCopyrightText: 2022 CERN and the Allpix Squared authors
# SPDX-License-Identifier: CC-BY-4.0
title: "Logging and Verbosity Levels"
weight: 8
---

Allpix Squared is designed to identify mistakes and implementation errors as early as possible and to provide the user with
clear indications about the problem. The amount of feedback can be controlled using different log levels which are inclusive,
i.e. lower levels also include messages from all higher levels. The global log level can be set using the global parameter
`log_level`. The log level can be overridden for a specific module by adding the `log_level` parameter to the respective
configuration section. The following log levels are supported:

- **FATAL**:
  Indicates a fatal error that will lead to direct termination of the application. Typically only emitted in the main
  executable after catching exceptions as they are the preferred way of fatal error handling (as discussed in
  [Section 4.9](../../04_framework/09_error_reporting)). An example of a fatal error is an invalid configuration parameter.

- **STATUS**:
  Important information about the status of the simulation. Is only used for messages which have to be logged in every run
  such as the global seed for pseudo-random number generators and the current progress of the run.

- **ERROR**:
  Severe error that should not occur during a normal well-configured simulation run. Frequently leads to a fatal error and
  can be used to provide extra information that may help in finding the problem (for example used to indicate the reason a
  dynamic library cannot be loaded).

- **WARNING**:
  Indicate conditions that should not occur normally and possibly lead to unexpected results. The framework will however
  continue without problems after a warning. A warning is for example issued to indicate that an output message is not used
  and that a module may therefore perform unnecessary work.

- **INFO**:
  Information messages about the physics process of the simulation. Contains summaries of the simulation details for every
  event and for the overall simulation. Should typically produce maximum one line of output per event and module.

- **DEBUG**:
  In-depth details about the progress of the simulation and all physics details of the simulation. Produces large volumes
  of output per event, and should therefore only be used for debugging the physics simulation of the modules.

- **TRACE**:
  Messages to trace what the framework or a module is currently doing. Unlike the DEBUG level, it does not contain any
  direct information about the physics of the simulation but rather indicates which part of the module or framework is
  currently running. Mostly used for software debugging or determining performance bottlenecks in the simulations.

- **PRNG**:
  This level enables printing of every single pseudo-random number requested from any generator used in the framework. This
  can be useful in order to investigate random number distribution among threads and events.

{{% alert title="Warning" color="warning" %}}
It is not recommended to set the `log_level` higher than **WARNING** in a typical simulation as important messages may be
missed. Setting too low logging levels should also be avoided since printing many log messages will significantly slow down
the simulation.
{{% /alert %}}

The logging system supports several formats for displaying the log messages. The following formats are supported via the
global parameter `log_format` or the individual module parameter with the same name:

- **SHORT**:
  Displays the data in a short form. Includes only the first character of the log level followed by the configuration
  section header and the message.

- **DEFAULT**:
  The default format. Displays system time, log level, section header and the message itself.

- **LONG**:
  Detailed logging format. Displays all of the above but also indicates source code file and line where the log message was
  produced. This can help in debugging modules.

More details about the logging system and the procedure for reporting errors in the code can be found in
[Section 4.8](../../04_framework/08_logging#logging-system) and [Section 4.9](../../04_framework/09_error_reporting).

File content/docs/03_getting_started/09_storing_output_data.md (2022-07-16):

---
# SPDX-FileCopyrightText: 2022 CERN and the Allpix Squared authors
# SPDX-License-Identifier: CC-BY-4.0
title: "Storing Output Data"
weight: 9
---

Storing the simulation output to persistent storage is of primary importance for subsequent reprocessing and analysis. Allpix
Squared primarily uses ROOT for storing output data, given that it is a standard tool in High-Energy Physics and allows
objects to be written directly to disk. The `ROOTObjectWriter` automatically saves all objects created in a `TTree`
\[[@roottree]\]. It stores separate trees for all object types and creates branches for every unique message name: a
combination of the detector, the module and the message output name as described in
[Section 4.7](../../04_framework/07_module_io). For each event, values are added to the leaves of the branches containing the
data of the objects. This allows for easy histogramming of the acquired data over the total run using standard ROOT
utilities.

Relations between objects within a single event are internally stored as ROOT TRefs \[[@roottref]\], allowing retrieval of
related objects as long as these are loaded in memory. An exception will be thrown when trying to access an object which is
not in memory. Refer to [Section 6.2](../../06_objects/02_object_history) for more information about object history.

In order to save all objects of the simulation, a `ROOTObjectWriter` module has to be added with a `file_name` parameter to
specify the file location of the created ROOT file in the global output directory. The file extension `.root` will be
appended if not present. The default file name is `data`, i.e. the file `data.root` is created in the output directory. To
replicate the default behaviour the following configuration can be used:

```ini
# The object writer listens to all output data
[ROOTObjectWriter]
# specify the output file (default file name is used if omitted)
file_name = "data"
```

The generated output file can be analyzed using ROOT macros. A simple macro for converting the results to a tree with
standard branches for comparison is described in
[Section 13.3](../../13_additional/root_analysis_macros#display-monte-carlo-hits-python).

It is also possible to read object data back in, in order to dispatch them as messages to further modules. This feature is
intended to allow splitting the execution of parts of the simulation into independent steps, which can be repeated multiple
times. The tree data can be read using a `ROOTObjectReader` module, which automatically dispatches all objects to the correct
module instances. An example configuration for using this module is:

```ini
# The object reader dispatches all objects in the tree
[ROOTObjectReader]
# path to the output data file, absolute or relative to the configuration file
file_name = "../output/data.root"
```

The Allpix Squared framework comes with a few more output modules which allow data storage in different formats, such as the
[`LCIOWriter`](../../07_modules/lciowriter) for the LCIO persistency event data model \[[@lcio]\], the
[`RCEWriter`](../../07_modules/rcewriter) for the native RCE file format \[[@rce]\], or the
[`CorryvreckanWriter`](../../07_modules/corryvreckanwriter) for the Corryvreckan reconstruction framework data format.
Consult [Chapter 7](../../07_modules) for all output modules.

[@roottree]: https://root.cern.ch/root/htmldoc/guides/users-guide/Trees.html
[@roottref]: https://root.cern.ch/root/htmldoc/guides/users-guide/InputOutput.html
[@lcio]: https://doi.org/10.1109/NSSMIC.2012.6551478
[@rce]: https://twiki.cern.ch/twiki/bin/view/Atlas/RCEDevelopmentLab

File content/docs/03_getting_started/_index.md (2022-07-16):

---
# SPDX-FileCopyrightText: 2022 CERN and the Allpix Squared authors
# SPDX-License-Identifier: CC-BY-4.0
title: "Getting Started"
description: "Get to know the basics of the framework."
weight: 3
---

This Getting Started guide is written with a default installation in mind, meaning that some parts may not apply if a custom
installation was used. When the `allpix` binary is used, this refers to the executable installed in `bin/allpix` in the
installation path. It is worth noting that before running any Allpix Squared simulation, ROOT and (in most cases) Geant4
should be initialized. Refer to [Section 2.4](../02_installation/04_initializing_dependencies) for instructions on how to
load these libraries.

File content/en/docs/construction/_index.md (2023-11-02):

---
# SPDX-FileCopyrightText: 2022 100µPET
# SPDX-License-Identifier: CC-BY-4.0
title: "Scanner Construction"
description: "Plans for ASIC integration into flex and tower assembly"
weight: 5
---

This section is meant to document the plans for the ASIC integration into the module, module into the tower, and tower into the scanner with mechanical supports, electronic and cooling services

Regaridng optimization of the scanner sensitivity, highly influenced by scanner geometry, it is important to note that its design should avoid scanner's regions with different stopping power for the annihilation photons, as illustrated below. This will provide a more uniform smapling region for the lines-of-response detected, making sensitivity compensation a second order correction.

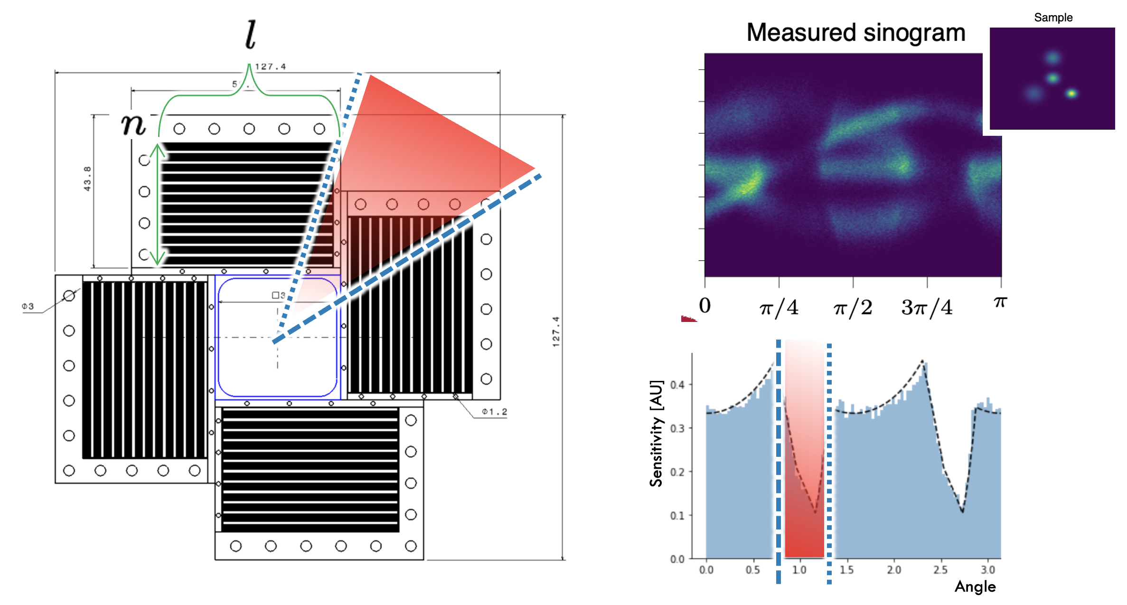
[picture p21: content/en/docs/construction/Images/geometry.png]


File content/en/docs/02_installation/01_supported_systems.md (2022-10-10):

---
# SPDX-FileCopyrightText: 2022 CERN and the Allpix Squared authors
# SPDX-License-Identifier: CC-BY-4.0
title: "Supported Operating Systems and Compilers"
weight: 1
---

## Operating Systems

```sh
git clone https://gitlab.cern.ch/allpix-squared/allpix-squared
cd allpix-squared
```

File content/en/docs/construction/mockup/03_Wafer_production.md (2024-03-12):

---
# SPDX-FileCopyrightText: 2022 100µPET
# SPDX-License-Identifier: CC-BY-4.0
title: "Wafer production"
weight: 3
---

## Introdiction
The wafer production is splitted in two:
- 4-inch wafers with Pt RTDs and Al heaters, maskless, produced by FCBG at NMP
- 6-inch wafers with Al heaters, with Cr mask, produced by us at CMi.

## Inventory

### 6-inch
We have started with 23 wafers in total, from a batch of 25 (two got brokem at the supplier).
</br>
20 wafers were coated by the supplier with 100 Å ±10% / 10,000 Å ±10% Ti / Al (sputtered).
</br>
The list below is the wafer thickness measured by the supplier after coating.
</br>
The wafers were delivered on a cassette with the same order as the list below.
<object data="../EH_measurements_box_1.pdf" type="application/pdf" width="100%" height="510px"></object>

The following list shows the status of each wafer.
| Wafer  | Where it is  | Production step    | Batch - Date | Comments                   |
|:-------|:-------------|:-------------------|:-------------|:---------------------------|
| 1      | CMi          | Ti/Al coated       |              |                            |
| 2      | CMi          | Ti/Al coated       |              |                            |
| 3      | CMi          | Ti/Al coated       |              |                            |
| 4      | CMi          | Ti/Al coated       |              |                            |
| 5      | CMi          | Ti/Al coated       |              |                            |
| 6      | CMi          | Ti/Al coated       |              |                            |
| 7      | CMi          | Ti/Al coated       |              |                            |
| 8      | CMi          | Ti/Al coated       |              |                            |
| 9      | CMi          | Ti/Al coated       |              |                            |
| 10     | CMi          | Ti/Al coated       |              |                            |
| 11     | CMi          | Ti/Al coated       |              |                            |
| 12     | CMi          | Ti/Al coated       |              |                            |
| 13     | CMi          | Ti/Al coated       |              |                            |
| 14     | CMi          | Ti/Al coated       |              |                            |
| 15     | UNIGE        | Ready for dicing   | #3 - 01/2024 | V2 mask                    |
| 16     | UNIGE        | Ready for dicing   | #3 - 03/2024 | V2 mask                    |
| 17     | UNIGE        | Ready for dicing   | #2 - 02/2024 | V2 mask                    |
| 18     | UNIGE        | Ready for dicing   | #1 - 01/2024 | Wrong mask, used for setup |
| 19     | UNIGE        | Ready for dicing   | #1 - 01/2024 | Wrong mask, used for setup - With Mateus |
| 20     | UNIGE        | Diced              | #1 - 01/2024 | Wrong mask, used for setup |

The remaining 3 wafers, delivered on a second cassette, also had their thickness measured.
<object data="../EH_measurements_box_2.pdf" type="application/pdf" width="100%" height="170px"></object>

| Wafer  | Where it is  | Production step    | Comments                   |
|:-------|:-------------|:-------------------|:---------------------------|
| 21     | UNIGE        | Bare silicon       |                            |
| 22     | UNIGE        | Bare silicon       |                            |
| 23     | UNIGE        | Bare silicon       |                            |

The list below tracks where the diced chips are.
<details>
<summary>Wafer #01</summary>
<pre>
|&nbsp;&nbsp;&nbsp;Chip&nbsp;&nbsp;&nbsp;|&nbsp;&nbsp;&nbsp;Where it is&nbsp;&nbsp;&nbsp;|&nbsp;&nbsp;&nbsp;Gold stud bumped?&nbsp;&nbsp;&nbsp;|&nbsp;&nbsp;&nbsp;Comments&nbsp;&nbsp;&nbsp;|
|:-----:|:------------:|:------------------:|:--------------------------:|
|  A2   | UNIGE        | No                 |                            |
|  A3   | UNIGE        | No                 |                            |
|  A4   | UNIGE        | No                 |                            |
|  B1   | UNIGE        | No                 |                            |
|  B2   | UNIGE        | No                 |                            |
|  B3   | UNIGE        | No                 |                            |
|  B4   | UNIGE        | No                 |                            |
|  B5   | UNIGE        | No                 |  With Franck for jig testing  |
|  C1   | UNIGE        | No                 |                            |
|  C2   | UNIGE        | No                 |                            |
|  C3   | UNIGE        | No                 |                            |
|  C4   | UNIGE        | No                 |  With Franck for jig testing  |
|  C5   | UNIGE        | No                 |  With Franck for jig testing  |
|  D2   | UNIGE        | No                 |                            |
|  D3   | UNIGE        | No                 |                            |
|  D4   | UNIGE        | No                 |  With Franck for jig testing  |
</pre>
</details>

### 4-inch
25 4-inch wafers were made available by Didier.
The following table list their thickness

|  Wafer | Thickness [um]  |
|:------:|:---------------:|
|  1     | 285             |
|  2     | 288             |
|  3     | 307             |
|  4     | 316             |
|  5     | 320             |
|  6     | 313             |
|  7     | 323             |
|  8     | 307             |
|  9     | 323             |
|  10    | 286             |
|  11    | 275             |
|  12    | 281             |
|  13    | 313             |
|  14    | 302             |
|  15    | 320             |
|  16    | 318             |
|  17    | 285             |
|  18    | 283             |
|  19    | 305             |
|  20    | 322             |
|  21    | 290             |
|  22    | 307             |
|  23    | 290             |
|  24    | 290             |
|  25    | 309             |

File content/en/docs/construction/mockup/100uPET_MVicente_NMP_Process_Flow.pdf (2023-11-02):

Lab : UNIGE - DPNC | Phone : 075 411 82 61
Operateur Name : Mateus Vicente | Office : DPNC
Supervisor Name : | E-mail : mateus.vicentebarretopinto@unige.ch

FCBG

## 100µPET test-chip

Description
Test-chip for the 100µPET project.

Neural Microsystems Platform’s machine needed
Plasma etcher (PINK), Sputter (AC 450), Semi-Automatic Coater, Mask exposure (MLA), developer, Dry etcher (Corial)
Substrate Type
4-inch Si wafer

Process Outline
Color chart
01 | Surface Preparation Machine: Plasma etcher (PINK) Recipe: 2min_High
02 | Metal deposition 10 nm Ti + 100 nm Pt Machine: Sputter (AC 450) Recipe:
03 | Dehydration & PR Coating Hot plate: 1min @ 110°C Machine: Semi_auto_coater Recipe: Baking:
Si | Ti | Pt | PR | Al | SiO2

Supervisor Name : | E-mail : mateus.vicentebarretopinto@unige.ch
04 | Mask Exposure + Develop Machine: MLA + developer Layer to expose: • Layer #3 Invert Mask polarity: Exposure window: 40 -40 40 -40 Dose: Development:
05 | Dry Etching Machine: Corial Recipe: Time:
06 | PR Stripping Ultrasonic bath & Acetone
07 | Dehydration & PR Coating Hot plate: 1min @ 110°C Machine: Semi_auto_coater Recipe: Baking:
08 | Mask Exposure + Develop Machine: MLA + developer Layer to expose: • Layer #134 Invert Mask polarity: Exposure window: See #04 Alignment Cross:

X Y
24000 36000
33000 18000
33000 -18000
-24000 | -36000
-33000 | -18000
-33000 | 18000
Dose:
Development:

Supervisor Name : | E-mail : mateus.vicentebarretopinto@unige.ch
09 | Metal deposition 10 nm Ti + 300 nm Al Machine: Sputter (AC 450) Recipe:
10 | Lift off Ultrasonic bath & Acetone
11 | Dehydration Machine: Hot plate Recipe: 110°C – 1 min
12 | Passivation coating 300 nm SiO2 Machine: Sputter (AC 450) Recipe: Baking:
13 | Dehydration & PR Coating Hot plate: 1min @ 110°C Machine: Semi_auto_coater Recipe: Baking:
14 | Mask Exposure + Develop Machine: MLA + developer Layer to expose: • Layer #9 Invert Mask polarity: Exposure window: See #04 Alignment Cross: See #08 Dose: Development:

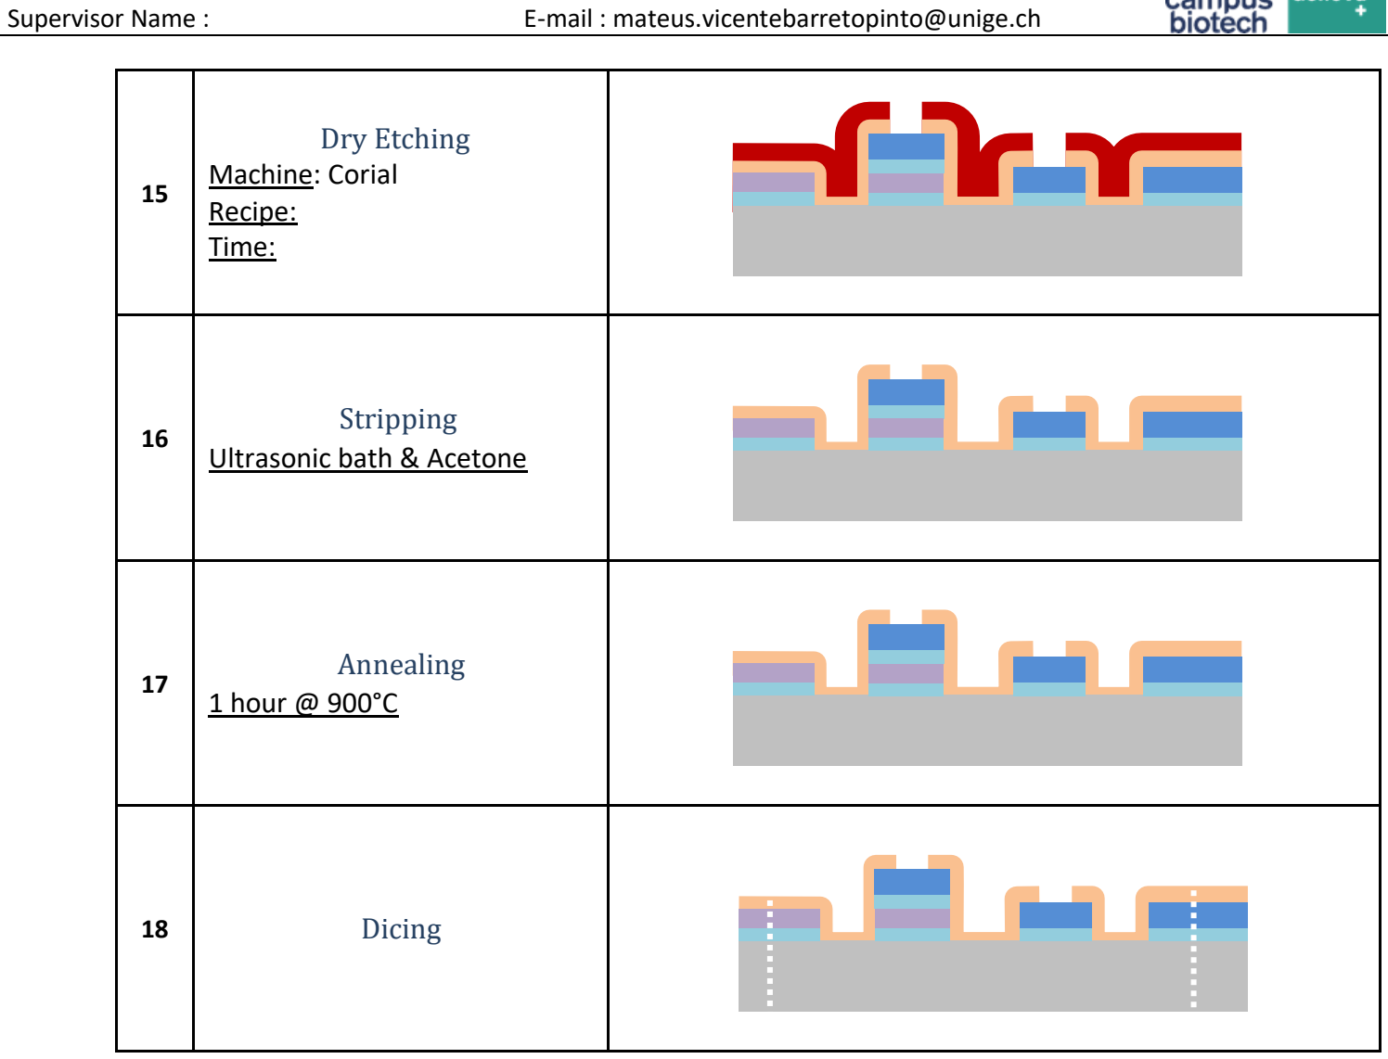
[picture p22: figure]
Supervisor Name :; E-mail : mateus.vicentebarretopinto@unige.ch; Stripping Ultrasonic bath & Acetone; Annealing 1 hour @ 900°C; 18 Dicing

15 | Dry Etching Machine: Corial Recipe: Time:

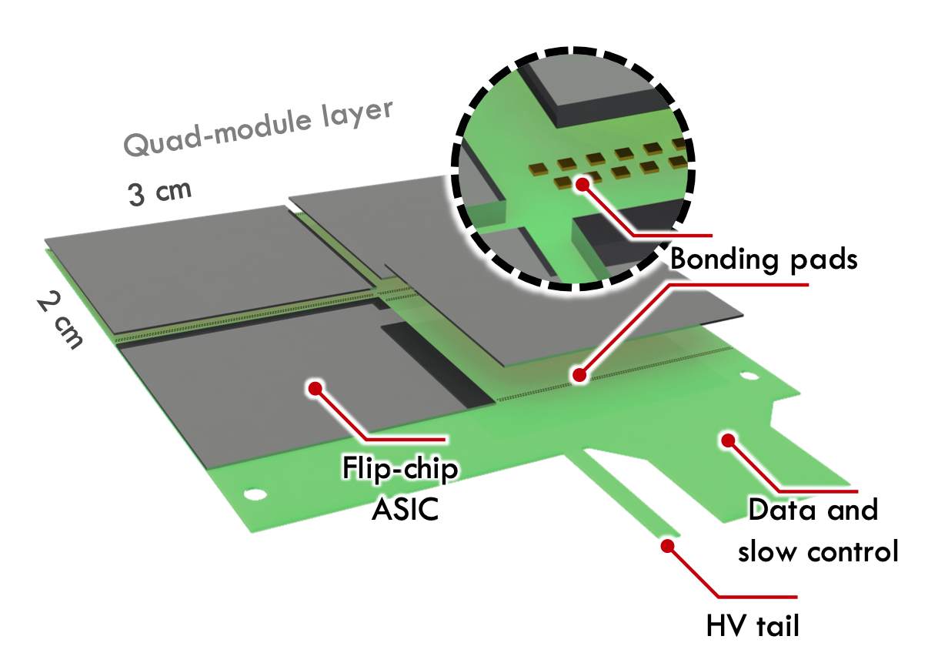
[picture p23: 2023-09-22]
content/en/docs/construction/Images/plane_flex.png

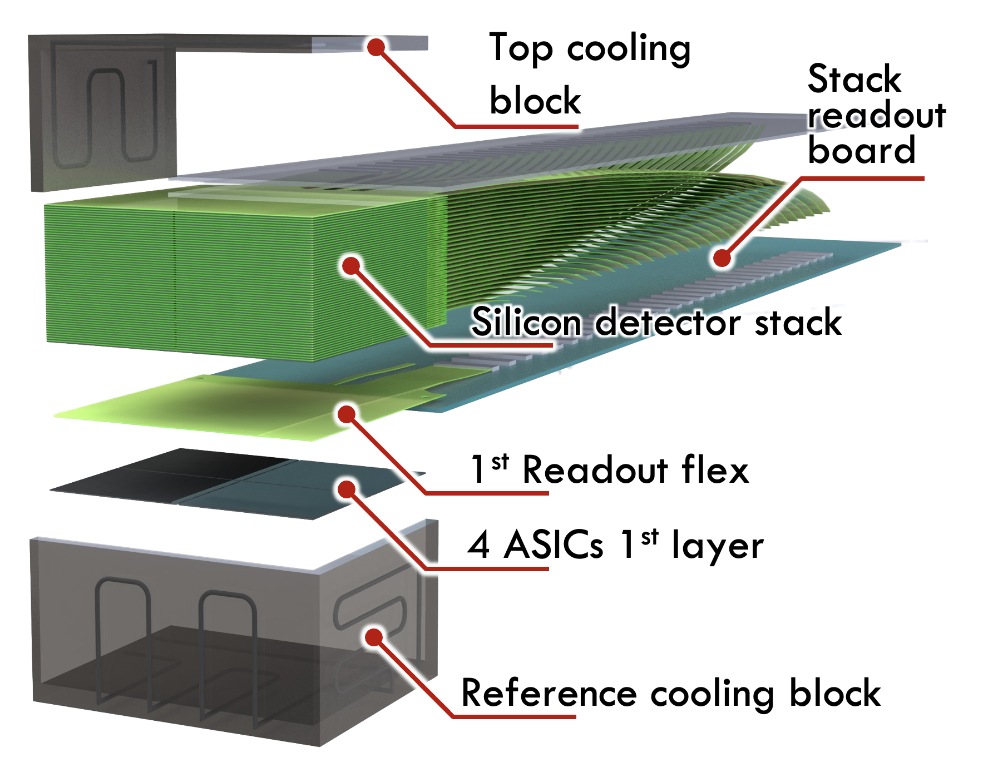
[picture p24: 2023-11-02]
content/en/docs/construction/Images/tower_assembly.png

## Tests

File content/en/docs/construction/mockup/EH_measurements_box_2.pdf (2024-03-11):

E+H

MX204-8-49-B-HR, #3767 | Version 2.836 (Build 1807)

E+H

# Metrology

Lot ID: 24-004.mn

Process step:default, ID #1 | Creation time of lot: 16.01.2024 12:28

Print date / time: 22.01.2024 10:12:06

| CntThk | AvgThk | TTV | Bow | BowX | BowY | Total Warp | PosWarp | NegWarp
21 | 301.38 | 301.91 | 1.65 | 5.38 | 3.93 | 4.13 | 25.33 | 10.99 | -14.35
22 | 300.88 | 301.67 | 2.86 | 5.19 | 2.05 | 4.23 | 25.74 | 11.63 | -14.11
23 | 303.88 | 304.29 | 3.10 | 5.40 | 4.08 | 4.13 | 24.09 | 10.24 | -13.84
C:\eh_app.3767\MXNT2\Reports\E+H.REP | Page 1

### Slot

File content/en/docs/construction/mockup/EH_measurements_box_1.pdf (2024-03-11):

E+H

MX204-8-49-B-HR, #3767 | Version 2.836 (Build 1807)

E+H

# Metrology

Lot ID: 24-004.mn

Process step:default, ID #1 | Creation time of lot: 16.01.2024 12:28

Print date / time: 22.01.2024 10:11:44

| CntThk | AvgThk | TTV | Bow | BowX | BowY | Total Warp | PosWarp | NegWarp
1 | 308.47 | 309.32 | 2.22 | -4.82 | -13.42 | -0.02 | 27.14 | 18.17 | -8.98
2 | 305.92 | 307.14 | 3.36 | -6.03 | -11.95 | -5.55 | 25.14 | 17.64 | -7.50
3 | 306.97 | 307.16 | 2.52 | -8.13 | -14.65 | -8.35 | 28.47 | 19.46 | -9.01
4 | 308.27 | 309.14 | 3.43 | -6.17 | -12.30 | -5.33 | 26.15 | 17.80 | -8.36
5 | 308.97 | 309.17 | 3.47 | -6.04 | -13.92 | -3.62 | 29.31 | 20.44 | -8.87
6 | 308.42 | 307.65 | 2.32 | -4.87 | -12.57 | -3.03 | 25.14 | 17.02 | -8.12
7 | 303.67 | 303.39 | 2.70 | -7.07 | -14.57 | -4.87 | 27.18 | 17.71 | -9.47
8 | 311.17 | 309.70 | 4.09 | -4.50 | -12.45 | -1.45 | 25.93 | 17.47 | -8.46
9 | 307.22 | 307.08 | 2.21 | -6.94 | -14.16 | -5.33 | 27.69 | 19.10 | -8.59
10 | 308.47 | 308.61 | 2.87 | -4.37 | -11.40 | -2.01 | 27.03 | 18.91 | -8.12
11 | 306.77 | 306.04 | 2.71 | -4.52 | -11.95 | -3.09 | 24.50 | 16.86 | -7.65
12 | 307.52 | 307.42 | 2.54 | -4.84 | -12.08 | -2.43 | 26.76 | 18.65 | -8.11
13 | 308.67 | 307.87 | 1.97 | -6.86 | -12.82 | -6.72 | 26.45 | 18.31 | -8.14
14 | 307.97 | 307.97 | 3.44 | -5.08 | -11.64 | -3.73 | 26.77 | 17.47 | -9.30
15 | 301.92 | 301.97 | 2.62 | -9.24 | -16.11 | -8.79 | 30.52 | 19.72 | -10.80
16 | 308.42 | 307.71 | 2.29 | -10.89 | -18.80 | -8.96 | 32.34 | 20.46 | -11.88
17 | 307.32 | 306.73 | 2.51 | -14.21 | -20.23 | -16.55 | 38.23 | 23.53 | -14.69
18 | 309.72 | 310.12 | 3.78 | -13.55 | -18.86 | -16.80 | 41.32 | 26.75 | -14.57
19 | 302.07 | 301.27 | 1.99 | -10.56 | -15.78 | -13.18 | 35.57 | 23.64 | -11.93
20 | 295.52 | 294.90 | 6.23 | -8.59 | -16.50 | -7.16 | 31.80 | 21.59 | -10.21
C:\eh_app.3767\MXNT2\Reports\E+H.REP | Page 1

### Slot

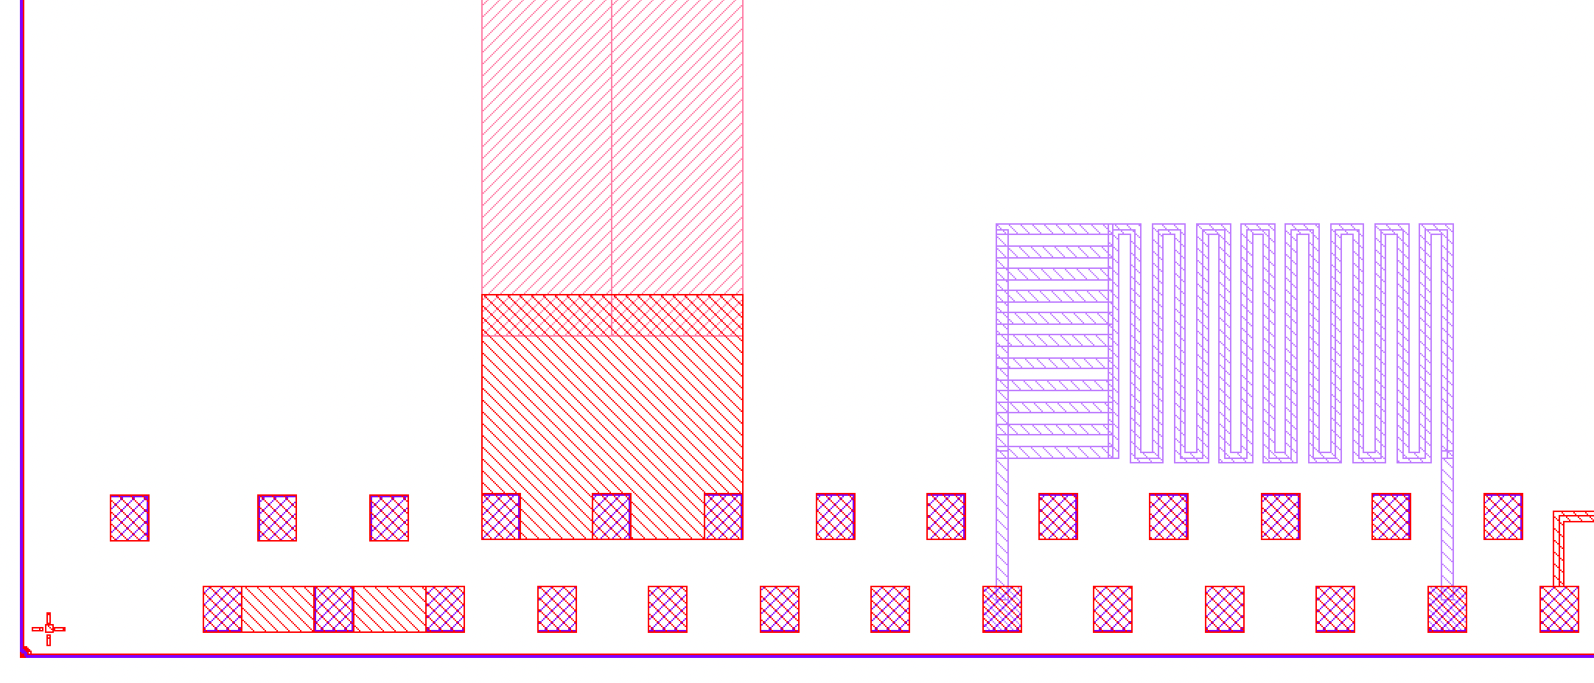
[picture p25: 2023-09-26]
content/en/docs/construction/mockup/test-chip2.png

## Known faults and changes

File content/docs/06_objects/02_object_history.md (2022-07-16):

---
# SPDX-FileCopyrightText: 2022 CERN and the Allpix Squared authors
# SPDX-License-Identifier: CC-BY-4.0
title: "Object History"
weight: 2
---

Objects may carry information about the objects which were used to create them. For example, a `PropagatedCharge` could hold
a link to the `DepositedCharge` object at which the propagation started. All objects created during a single simulation event
are accessible until the end of the event; more information on object persistency within the framework can be found in
[Section 4.6](../../04_framework/06_messages#persistency).

Object history is implemented using the ROOT TRef class \[[@roottref]\], which acts as a special reference. On construction,
every object gets a unique identifier assigned, that can be stored in other linked objects. This identifier can be used to
retrieve the history, even after the objects are written out to ROOT TTrees \[[@roottree]\]. TRef objects are however not
automatically fetched and can only be retrieved if their linked objects are available in memory, which has to be ensured
explicitly. Outside the framework this means that the relevant tree containing the linked objects should be retrieved and
loaded at the same entry as the object that request the history. Whenever the related object is not in memory (either because
it is not available or not fetched) a `MissingReferenceException` will be thrown.

A MCTrack which originated from another MCTrack is linked via a reference to this track, this way the track hierarchy can be
obtained. Every MCParticle is linked to the MCTrack it is associated with. A MCParticle can furthermore be linked to another
MCParticle on the same detector. This will be the case if there are MCParticles from a primary (parent) and secondary (child)
track on one detector. The corresponding child MCParticles will then carry a reference to the parent MCParticle.

[@roottref]: https://root.cern.ch/root/htmldoc/guides/users-guide/InputOutput.html
[@roottree]: https://root.cern.ch/root/htmldoc/guides/users-guide/Trees.html

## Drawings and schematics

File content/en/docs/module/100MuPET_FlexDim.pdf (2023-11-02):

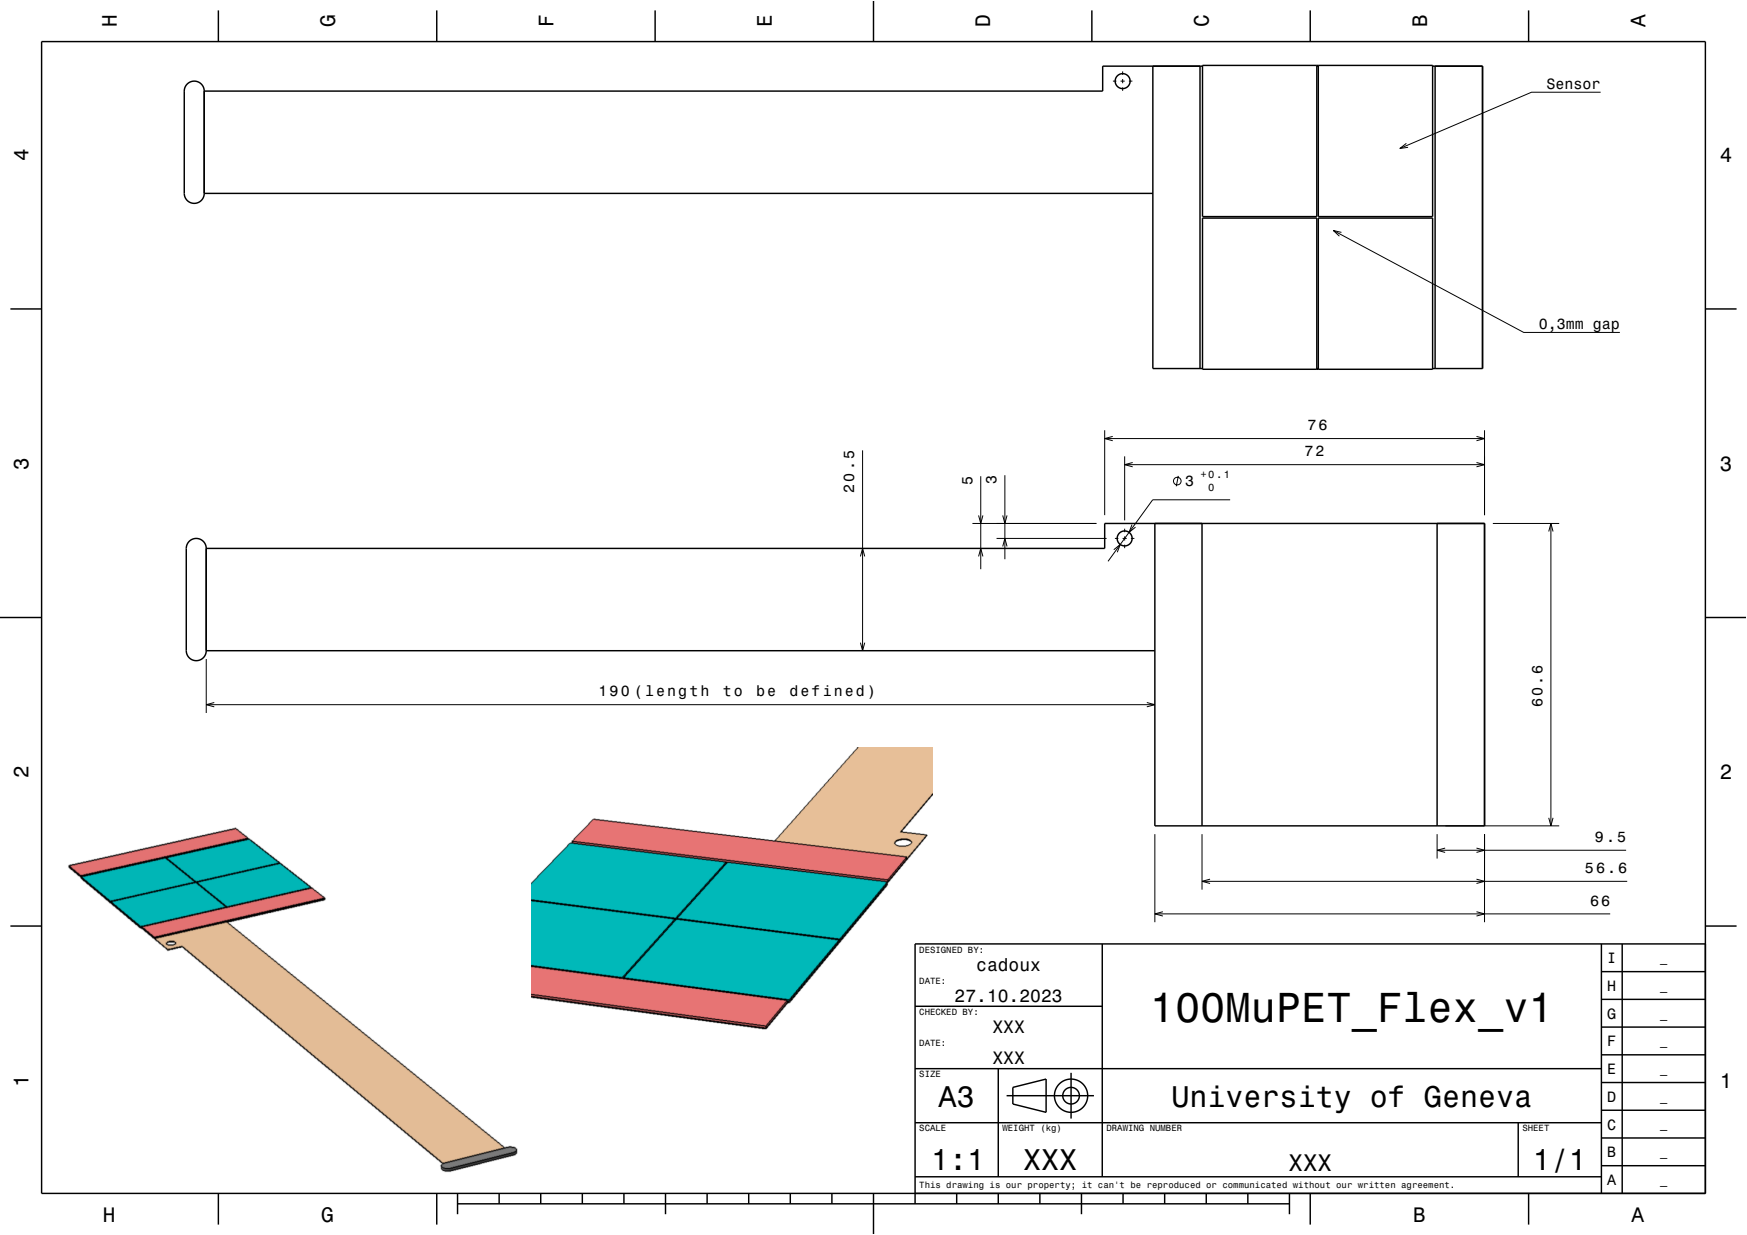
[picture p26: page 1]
CHECKED BY:; 0,3mm gap

190 (length to be defined)

DESIGNED BY: cadoux DATE: 27.10.2023 | 100MuPET_Flex_v1 | I | _

SIZE A3 | | | | University of Geneva

SCALE 1:1 | WEIGHT (kg) XXX | DRAWING NUMBER XXX | SHEET 1/1

This drawing is our property; it can't be reproduced or communicated without our written agreement.

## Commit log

2023-09-05 including detector assembly
2023-09-14 adding models and data folder
    [Mouse_phantom_AA_80x19x34_1000um.3dm, Mouse_phantom_A_80x19x34_1000um.3dm, Mouse_phantom_BB_160x38x68_500um.3dm, Mouse_phantom_B_160x38x68_500um.3dm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]
2023-11-02 Specs doc imported and updated - WIP
    [IO_pads_100uPET.xlsx]
